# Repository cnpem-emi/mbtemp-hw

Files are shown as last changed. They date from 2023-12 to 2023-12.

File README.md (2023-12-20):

MBTemp
=====

MBTemp is an electronic board to acquire temperature in eight independent channels. It has been developed by the Control Group of Brazilian Synchrotron Light Laboratory (LNLS).

Example
-------

An example of use is present in the well documented file `exemplo-mbtemp.py`.

Contacts
-------------------------------------

Any doubts related to this projects, please do not hesitate to contact Robert Polli (robert.polli@cnpem.br)

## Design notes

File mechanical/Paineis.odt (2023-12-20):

PAINEL MBTemp

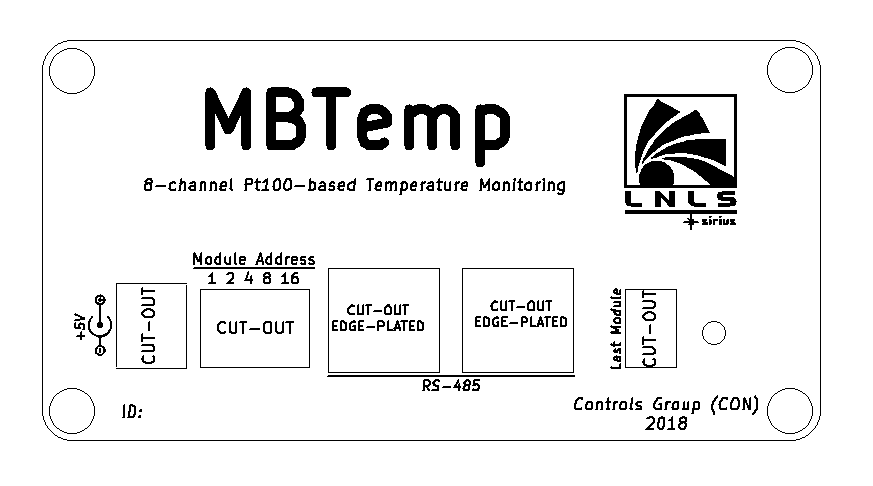
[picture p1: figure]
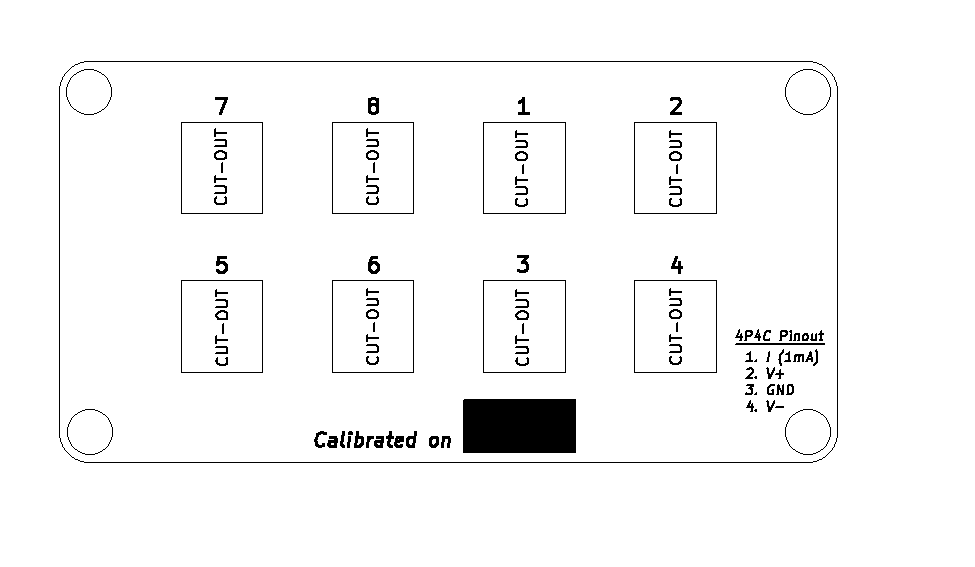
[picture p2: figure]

PAINEL MBTemp

v2

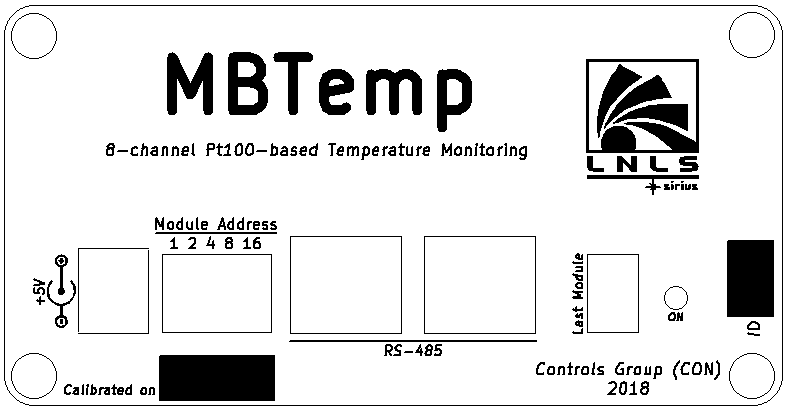
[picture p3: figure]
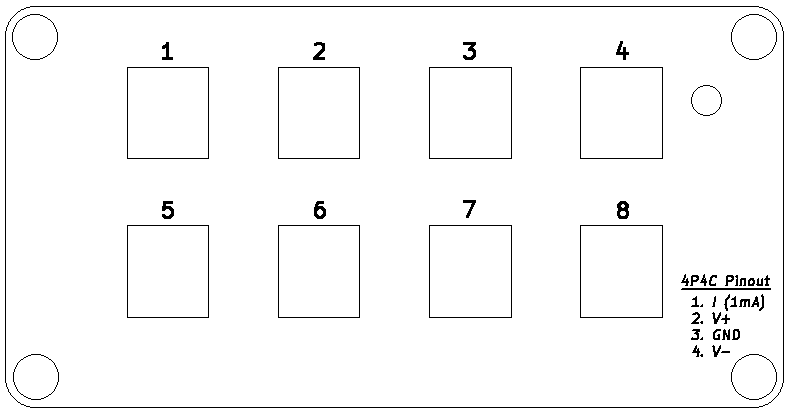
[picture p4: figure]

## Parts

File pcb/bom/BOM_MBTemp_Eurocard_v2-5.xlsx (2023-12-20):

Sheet: MBTemp3_Eurocard
Designator | Description | Value | Part Number | Package | Manufacturer | Quantity | PN CNPEM | Obs
C13,C12 | Ceramic Capacito 20pF 50V 5% SMD 0805 NP0 | 20pF | CL21C200JBANNNC | 0805 | Samsung ElectroMechanics | 2 | MT104425
C25 | Ceramic Capacitor 56pF 50V 5% SMD 0805 NP0 | 56pF | CL21C560JBANNNC | 0805 | Samsung ElectroMechanics | 1 | MT104427
C26,C23,C21,C17,C29,C34 | Multilayer Ceramic Capacitor 100nF 50V ±5% SMD 0805 X7R | 100nF | 08055C104JAT2A | 0805 | AVX | 6 | MT104382
C27,C24,C22,C18,C2,C15,C14,C1,C8,C11,C201,C37,C39,C47,C48,C41,C42,C45,C46,C61,C60,C59,C58,C57,C56,C55,C54 | Ceramic Capacitor 10uF 16V ±10% SMD 0805 X5R | 10uF | CL21A106KOQNNNE | 0805 | Samsung ElectroMechanics | 27 | MT104058
C28 | Aluminium Radial Capacitor 470uF 16V 20% PTH | 470uF | ECA-1CM471 | Radial Can | Panasonic Electronic Components | 1 | MT104059
C30,C31,C32,C3,C16,C10,C9,C38,C43,C44,C53,C20,C19 | Ceramic Capacitor 1uF 16V ±5% SMD 0805 X7R | 1u | C0805C105J4RACTU | 0805 | Kemet | 13 | MT104060
C33,C35 | Multilayer Ceramic Capacitor 47nF 100V 5% SMD 0805 X7R | 47nF | 08051C473JAT2A | 0805 | AVX | 2 | MT104243
C36 | Tantalum Capacitor 10uF, 10V, 10%, ESR 3.8ohm | 10uF | T491A106K010AT7280 | 1206 | Kemet | 1 | AP111595
C4,C7 | Ceramic Capacitor 4.7uF 50V 10% SMD 1210 X7R | 4.7uF | GRM32ER71H475KA88L | 1210 | Murata | 2 | MT104428
C40,C49 | Ceramic Capacitor 22nF 100V 5% SMD 0805 X7R | 22n | 08051C223JAT2A | 0805 | Murata | 2 | MT104429
C50,C51,C52 | Ceramic Capacitor 100pF 50V 5% SMD 0805 NP0 | 100pF | C0805C101J5GACTU | 0805 | Kemet | 3 | MT104242
C6,C5 | Ceramic Capacitor 10nF 50V 5% SMD 0805 C0G | 10nF | GRM2195C1H103JA01D | 0805 | Murata | 2 | AP111901
D1 | Green LED, 2.1V, 20mA, SMD 0805 | LED Green | LTST-C171GKT | 0805 | Lite-On Inc | 1 | AP111654
D2 | LED Circuit Board Indicator Single Red Diffused, Through Hole, Right Angle | LED Red | WP934CB/ID | 2x1 PTH pitch 2,54mm | Kingbright | 1 | AP110389
D4,D5 | Diodo Schottky 20V 500mA DC SMD 0805 | Diode Sch | SD0805S020S0R5 | 0805 | AVX Corporation | 2 | AP103285
J4,J3,J6,J5 | RJ11 Jack connector Right Angle | RJ11 | TM5RJ3-44(50) | 4P4C | Hirose Electric Co | 4 | AP110402
J9,J10 | RJ25 | RJ25 | 133623 | 6P6C | ERNI | 2 | AP109847
JP1 | Dip Switch SPST 2 Position Through Hole, Right Angle Slide (Standard) Actuator 25mA 24VDC | DIP switch 2pos Right Angle | KAS2102E | DIP Switch Right Angle PTH | E-Switch | 1 | AP110400
K1 | Power Barrel Jack Connector 2mm ID, 5.5mm OD, PTH, right angle | Jack | PJ-002AH | Jack J4-5.5mm 2.0mm | CUI Inc | 1 | MT104062
L2,L1 | 6.8uH shielded wirewound Inductor 850mA 288mOhm | 6.8uH | LQH32PN6R8NN0L | 1210 | Murata | 2
P1 | DIP Switch slide 5 positions SPST right angle PTH | DIP Switch slide SPST right angle PTH | KAS2105E | PIN_ARRAY_5x2 | E-Switch | 1 | MT103732
P2 | 10 positions Male Header, PTH, Shrouded Connector, Pitch 2.54mm | Header 2x05 | 302-S101 | Straight_2x05 Shrouded pitch 2.54mm | On Shore Technology Inc | 1 | AP103279
P3 | Conector 2x10 pitch 2.54mm | CONN_02X10 | DW-10-09-F-D-425 | Pin_Header_Straight_2x10 | Samtec | 1 | MT104063
P4 | Pino de testes | 1 pin |  | Pin Header Straight 1x1 |  | 1 | ---- | NÃO DEVE SER MONTADO/COMPRADO
R1 | Resistor 22K ohm 0,1% 1/8W SMD 0805 Thin Film | 22kΩ | ERA-6AEB223V | 0805 | Panasonic Electronic Components | 1 | MT104109
R17,R16,R24,R36,R45,R27 | Resistor Jumper 0 ohm 1% 1/8W SMD 0805 Thick Film | 0Ω | RC0805JR-070RL | 0805 | Yageo | 6 | MT100803
R19,R18,R25,R35,R44,R32 | Resistor Jumper 0 ohm 1% 1/8W SMD 0805 Thick Film | 0 | RC0805JR-070RL | 0805 | Yageo | 6 | ---- | NÃO DEVE SER MONTADO/COMPRADO
R2 | Resistor 100 ohm 0,1% 1/8W SMD 0805 Thin Film | 100Ω | ERA-6AEB101V | 0805 | Panasonic Electronic Components | 1 | MT104084
R20,R14 | Resistor 1 Mohm 1% 1/8W SMD 0805 Thick Film | 1MΩ | RC0805FR-071ML | 0805 | Yageo | 2 | MT104430
R15,R5 | Resistor 1K ohm 0,1% 1/8W SMD 0805 Thin Film | 1kΩ | ERA-6AEB102V | 0805 | Panasonic Electronic Components | 2 | MT104085
R21,R22 | Resistor 1K ohm 1% 1/8W SMD 0805 Thick Film | 1kΩ | RC0805FR-071KL | 0805 | Yageo | 2 | MT104228
R23 | Resistor 470 ohm 1% 1/8W SMD 0805 Thick Film | 470Ω | RC0805FR-07470RL | 0805 | Yageo | 1 | MT104431
R40 | Resistor 620 ohm 1% 1/8W SMD 0805 Thick Film | 620Ω | RC0805FR-07620RL | 0805 | Yageo | 1 | MT104227
R29 | Resistor 2.2 k ohm 1% 1/8W SMD 0805 Thick Film | 2.2kΩ | RC0805FR-072K2L | 0805 | Yageo | 1 | MT104237
R3 | Resistor 120 ohm 0,1% 1/8W SMD 0805 Thin Film | 120Ω | ERA-6AEB121V | 0805 | Panasonic Electronic Components | 1 | MT104086
R26 | Resistor 120 ohm 1% 1/8W SMD 0805 Thick Film | 120Ω | RC0805FR-07120RL | 0805 | Yageo | 1 | MT104234
R30 | Resistor 33 k ohm 1% 1/8W SMD 0805 Thick Film | 33kΩ | RC0805FR-0733KL | 0805 | Yageo | 1 | MT104432
R31 | Resistor 4.7 k ohm 1% 1/8W SMD 0805 Thick Film | 4.7kΩ | RC0805FR-074K7L | 0805 | Yageo | 1 | MT104433
R34 | Resistor 910 k ohm 1% 1/8W SMD 0805 Thick Film | 910kΩ | RC0805FR-07910KL | 0805 | Yageo | 1 | MT104231
R38, R39 | Resistor 300k ohm ±0,1% 1/8W SMD 0805 Thin Film | 300kΩ | RT0805BRD07300KL | 0805 | Yageo | 1 | MT104087
R43 | Resistor 62 k ohm 1% 1/8W SMD 0805 Thick Film | 62kΩ | RC0805FR-0762KL | 0805 | Yageo | 1 | MT104434
R6,R7 | Resistor 6.2 k ohm 0,1% 1/8W SMD 0805 Thin Film | 6.2kΩ | ERA-6AEB622V | 0805 | Panasonic Electronic Components | 2 | MT104088
R8,R4 | Resistor 330 ohm, 0,1%, 1/8W, SMD 0805, Thin Film | 330Ω | ERA-6AEB331V | 0805 | Panasonic Electronic Components | 2 | MT104089
R9,R10,R11,R12,R13,R28,R42 | Resistor 10K ohm 1% 1/8W SMD 0805 Thick Film | 10kΩ | RC0805FR-0710KL | 0805 | Yageo | 7 | MT104235
SW1,SW2 | 3 positions header connector 0.1” PTH Gold | -5V / +6V | 961103-6404-AR | Pin_Header_Straight_1x03_Pitch2.54mm | 3M | 2 | MT104065
U10 | 5V Voltage Reference IC +/-0.05% 10mA | REF5050 | REF5050IDR | SOIC-8 | Texas Instruments | 1 | AP100206
U11 | General Purpose Amplifier 2 Circuit | OPA2277 | OPA2277UA/2K5 | SOIC-8 | Texas Instruments | 1 | AP102160
U12 | Differential Amplifier 1 Circuit Differential Rail-to-rail | AD8139 | AD8139ARDZ-REEL7 | SO-8 Expoded Pad | Analog Devices | 1 | AP103263
U13 | Analog to Digital Converter 16 bits SAR | ADS8318 | ADS8318IBDGST | MSOP-10 | Texas Instruments | 1 | AP103262
U14 | DCDC Converter IC, 1W, 5V output, 5V input | DCR010505U | DCR010505U/1K | SOIC-28 | Texas Instruments | 1 | AP109804
U15 | Linear Regulator LDO Adjustable Negative 1,5A | LT3015 | LT3015EMSE#PBF | MSOP-12 | Linear Technology | 1 | AP107414
U19 | Linear Regulator LDO Adjustable Negative 1,5A | LT3015 | LT3015EMSE#PBF | MSOP-12 | Linear Technology | 1 | ---- | NÃO DEVE SER MONTADO/COMPRADO
U16 | DCDC Converter IC, 1W, +/-12V output, 5V input | DCP010512D | DCP010512DBP-U | DCP010512D | Texas Instruments | 1 | AP106621
U9,U18 | Linear Voltage Regulator Adjustable IC, 0-36V, 1.1A, SMD SOT-223 | LT3080 | LT3080EST#TRPBF | SOT-223 | Linear Technology | 2 | MT104255
U17 | Linear Voltage Regulator Adjustable IC, 0-36V, 1.1A, SMD SOT-223 | LT3080 | LT3080EST#TRPBF | SOT-223 | Linear Technology | 1 | ---- | NÃO DEVE SER MONTADO/COMPRADO
U2,U1,U3 | Circuit IC Switch 8:1 120ohms | 74HC4051 | 74HC4051PW,118 | TSSOP-16 | NXP | 3 | AP103267
U4 | Current Source Regulator IC 200mA 1% | LT3092 | LT3092EST#PBF | SOT-223 | Linear Technology | 1 | AP103266
U5 | 2.5V Voltage Reference IC +/-1% 10mA | REF5025 | REF5025AQDRQ1 | SOIC-8 | Texas Instruments | 1 | AP103265
U6 | RS422/485 Digital Isolator IC, 2500Vrms, 40Mbps, SMD SOIC-16 | IL3685 | IL3685E | SOIC-16 | NVE | 1 | AP102999
U7 | PIC 16F Microcontroller 8-bit 20MHz 14kB Flash | PIC16F887A_TQFP | PIC16F887-I/PT | TQFP-44 | Microchip Technology | 1 | AP103857
U8 | Switching regulator Buck-Boost Adjustable | LT3582 | LT3582EUD#PBF | WFQFN-16 | Linear Technology | 1 | AP100196
X1 | 16MHz +/- 30ppm Crystal 20pF 40ohm SMD | CRYSTAL 16MHz | ECS-160-20-5PX-TR | CrystalSMD HC49/US | ECS Inc | 1 | MT104066
F1,F2,F3,F4 | Fiducial 1mm | NA | NA | NA | NA | 4

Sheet: MBTemp_Stack
Designator | Description | Value | Part Number | Package | Manufacturer | Quantity | PNCNPEM | Obs
J2,J1,J8,J7 | RJ11 Jack connector Right Angle | RJ11 | TM5RJ3-44(50) | 4P4C | Hirose Electric Co | 4 | AP110402
P3 | Conector 2x10 pitch 2.54mm | CONN_02X10 | SSQ-110-03-F-D | Pin_Header_Straight_2x10 | Samtec | 1 | MT104067
C1,C2,C3,C4,C5,C6,C7,C8 | Ceramic Capacitor 10uF 16V ±10% SMD 0805 X5R | 10uF | CL21A106KOQNNNE | 0805 | Samsung ElectroMechanics | 8 | MT104058
F1,F2,F3,F4 | Fiducial 1mm | NA | NA | NA | NA | 4
 |  |  |  |  |  | "

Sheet: Montagem Mecanica
Designator | Description | Value | Part Number | Package | Manufacturer | Quantity | PN CNPEM | Obs
MH5,MH6,MH7 | Montagem Mecânica M3 | Espaçador 19mm M3x0.5 steel | 971190321 | M3 | Wurth Electronics Inc | 3 | MT103722
 |  | MACHINE SCREW PAN PHILLIPS M3 | MPMS 003 0005 PH | M3 | B&F Fastener Supply | 3 | AO104596
 |  | HEX NUT 0.217" M3 | MHNZ 003 | M3 | B&F Fastener Supply | 3 | MT103727
 |  | Arruela para parafusos M3 | MFWZ 003 | M3 | B&F Fastener Supply | 6 | MT103728 | Para colocar no parafuso e porca
Jumper | Jumper for SW1 and SW2 | Connector jumper 2.54mm – Flash Gold | QPC02SXGN-RC | Jumper | Sullins Connector | 2 |  | Conectado ao pino “LIN”

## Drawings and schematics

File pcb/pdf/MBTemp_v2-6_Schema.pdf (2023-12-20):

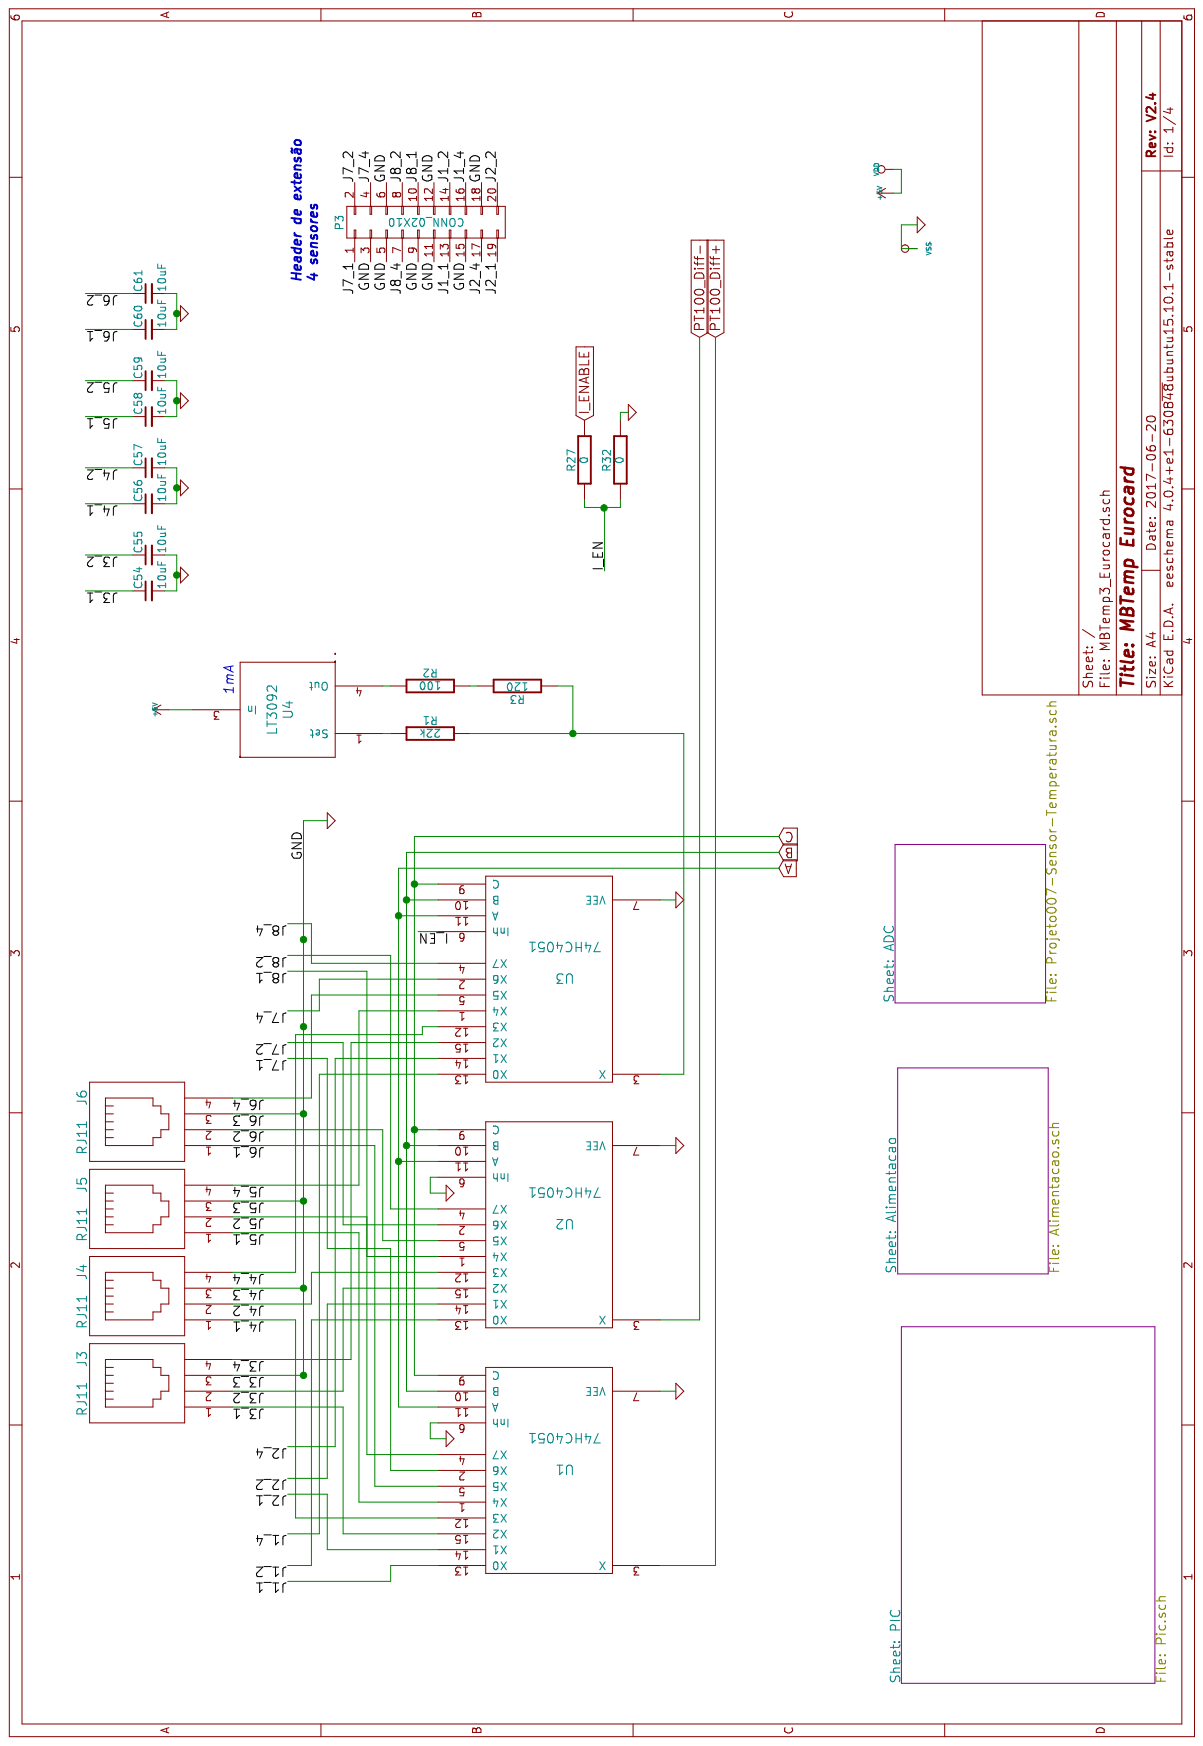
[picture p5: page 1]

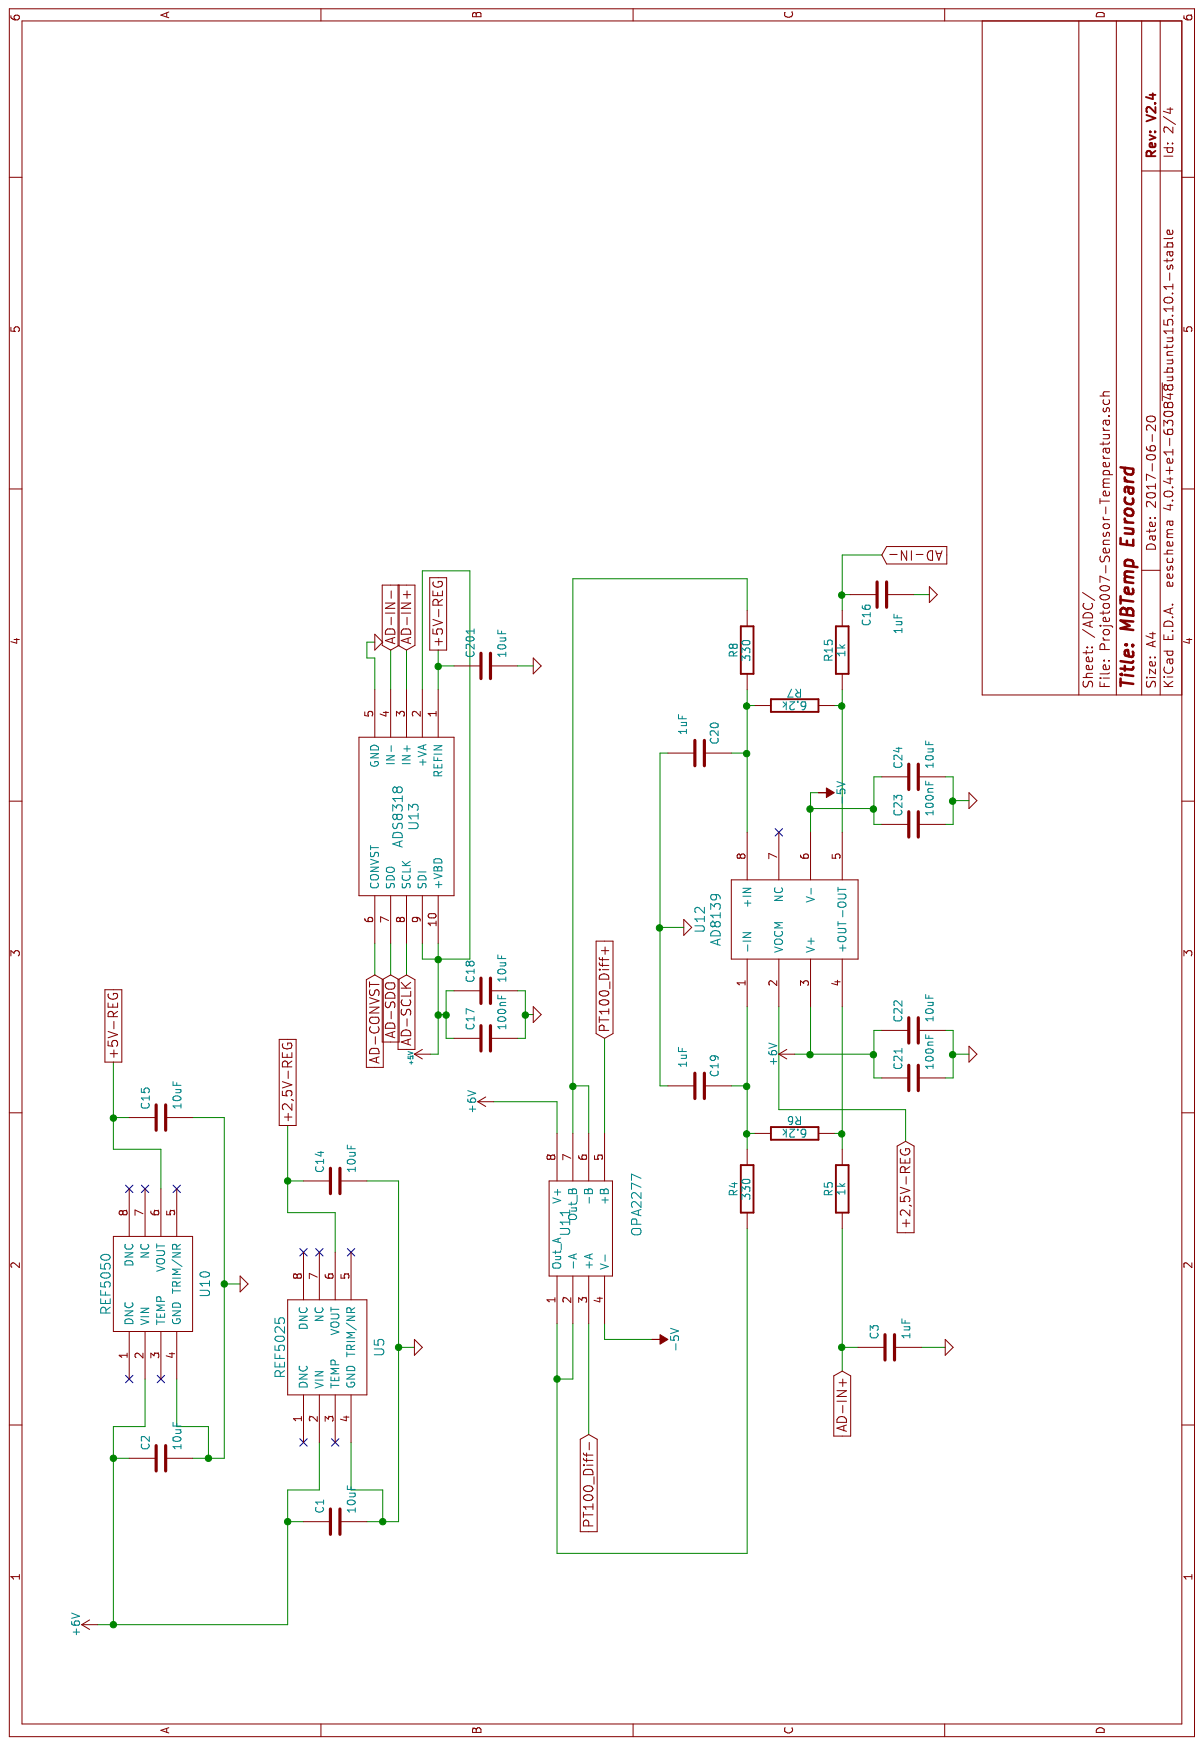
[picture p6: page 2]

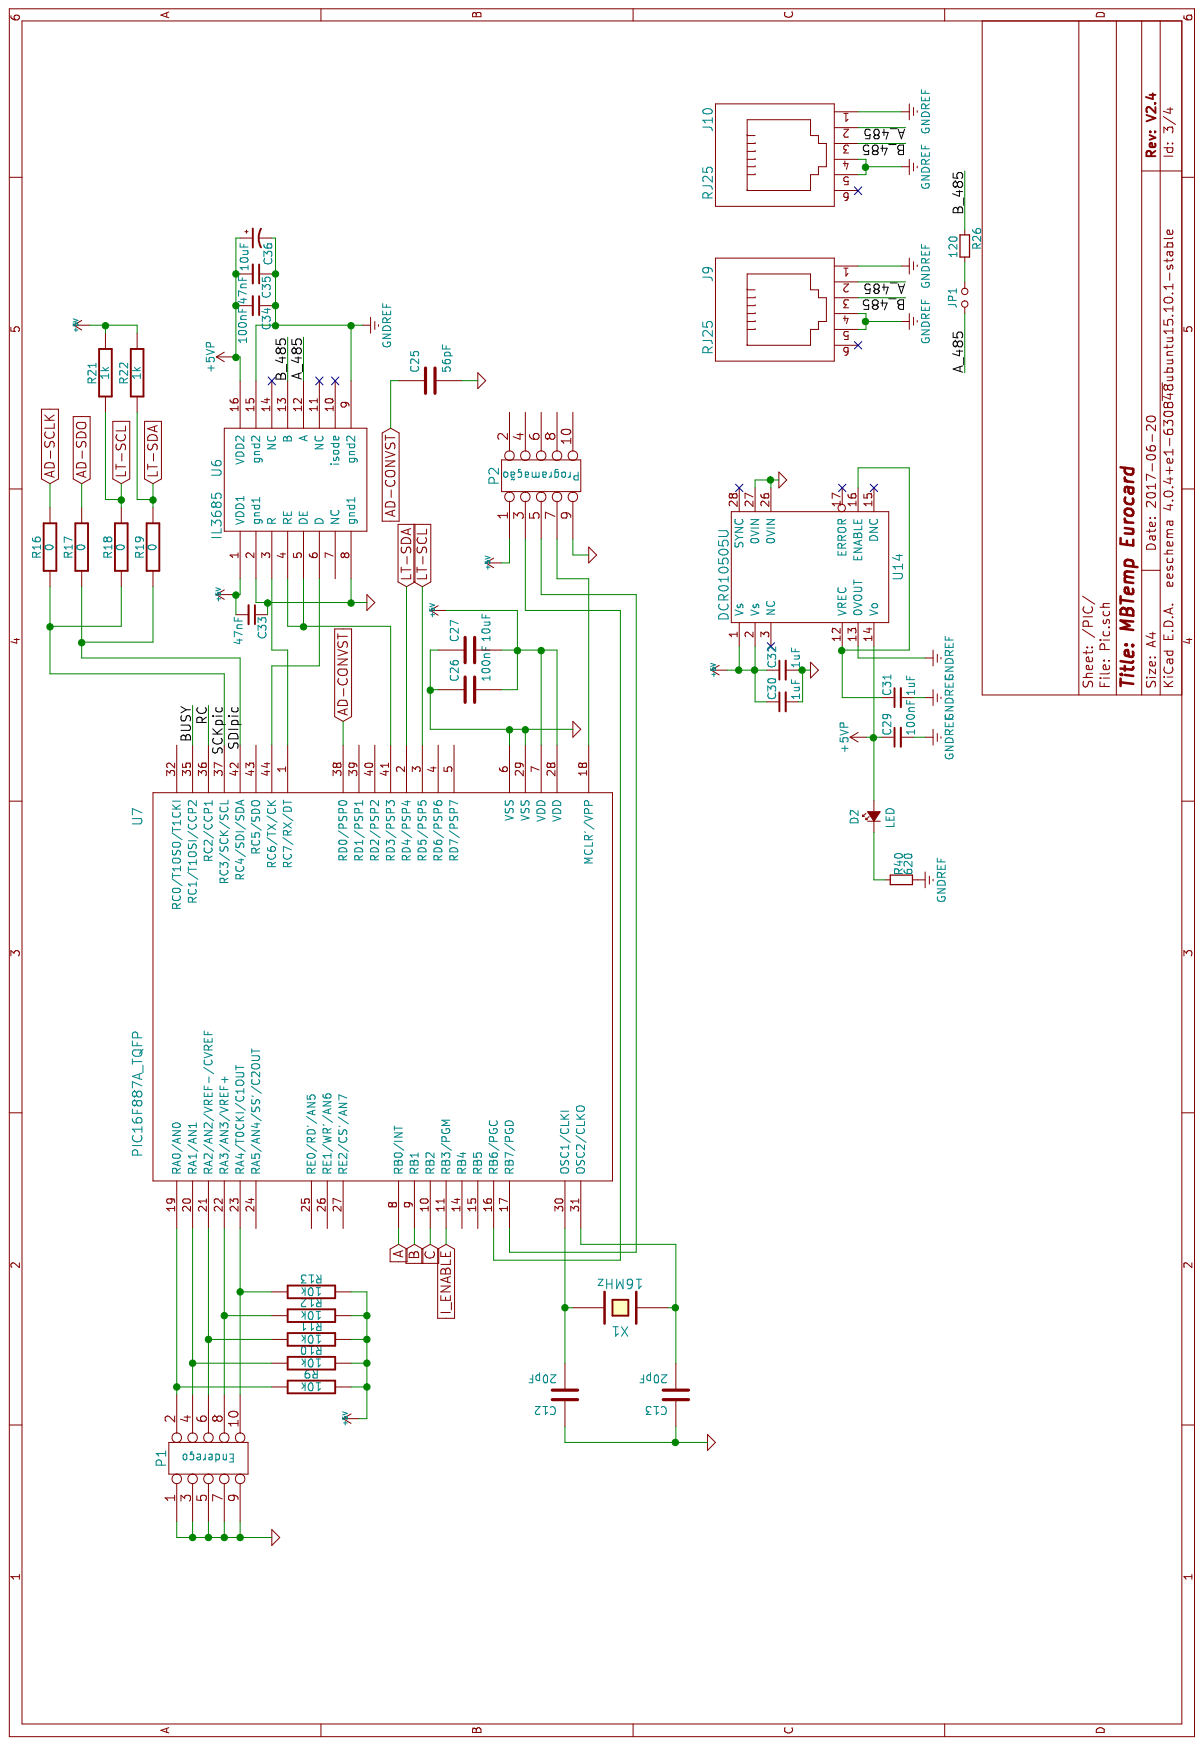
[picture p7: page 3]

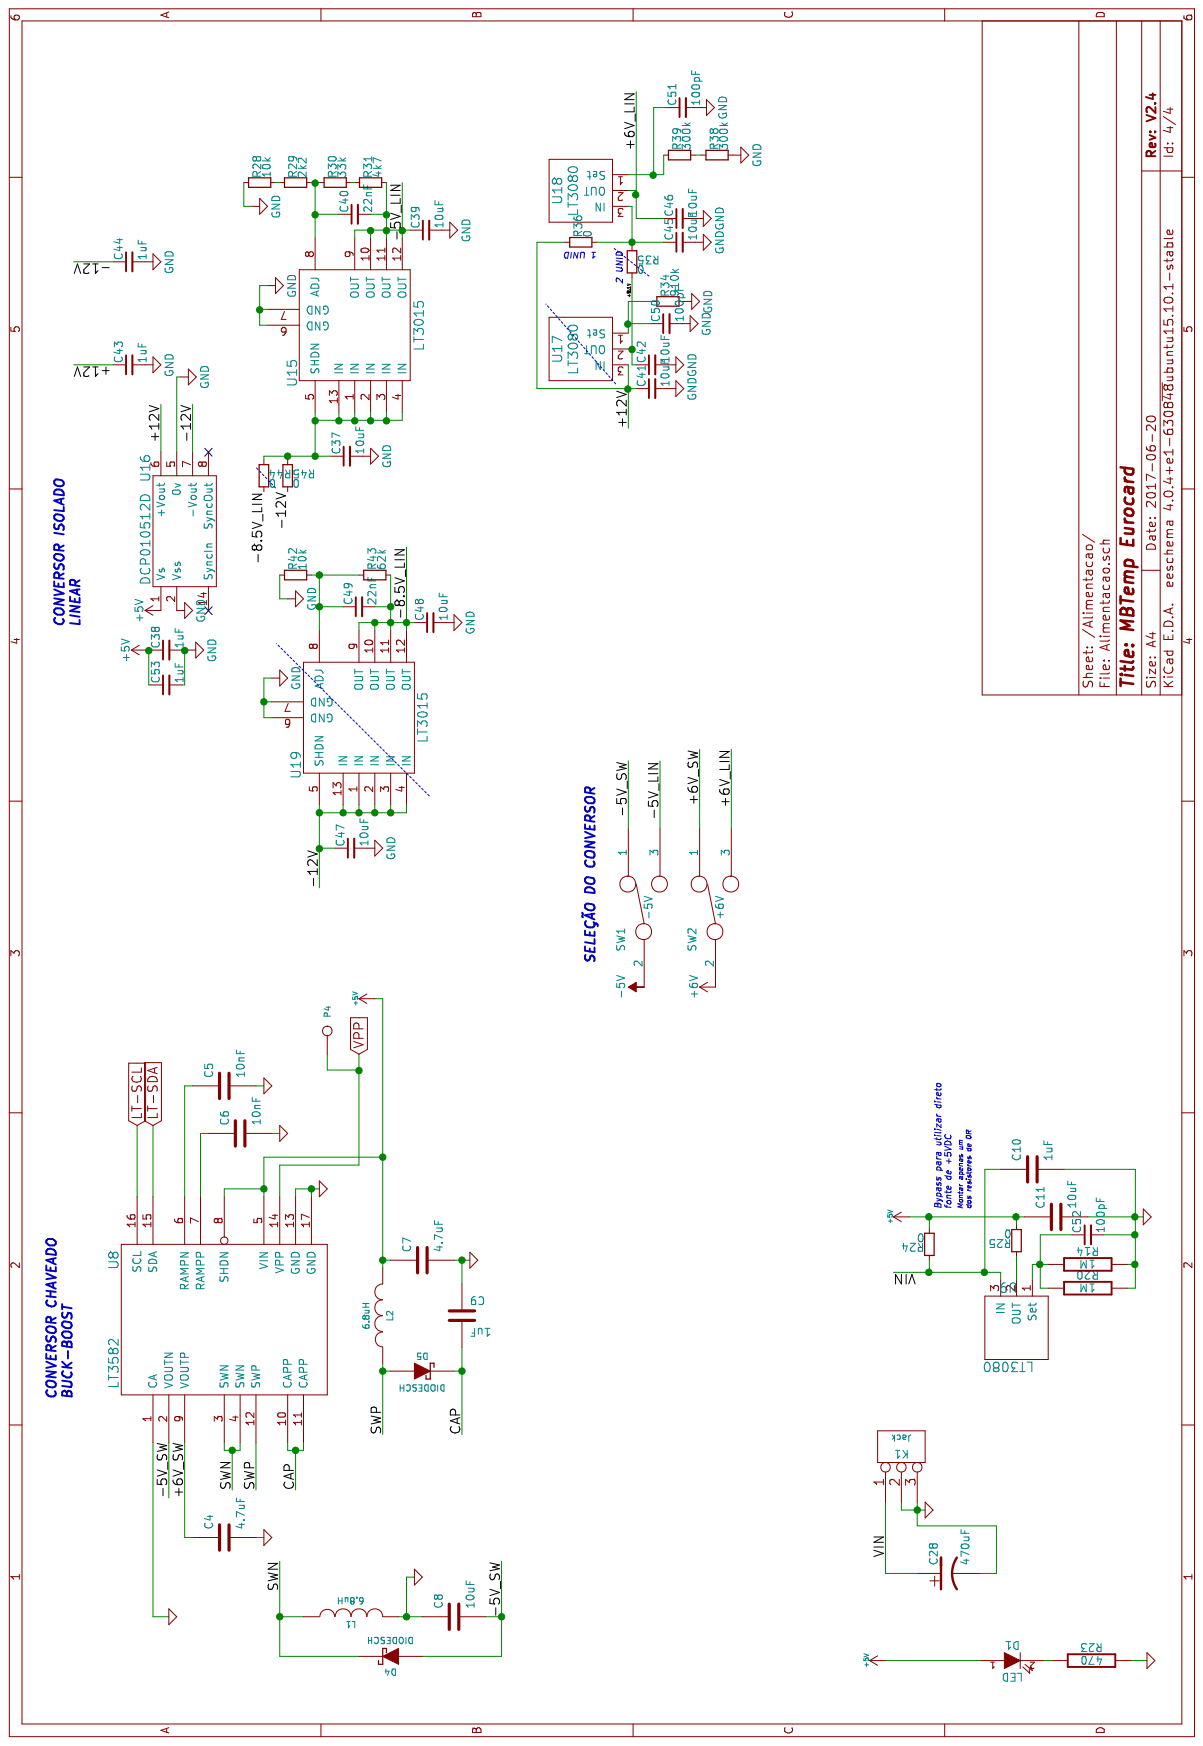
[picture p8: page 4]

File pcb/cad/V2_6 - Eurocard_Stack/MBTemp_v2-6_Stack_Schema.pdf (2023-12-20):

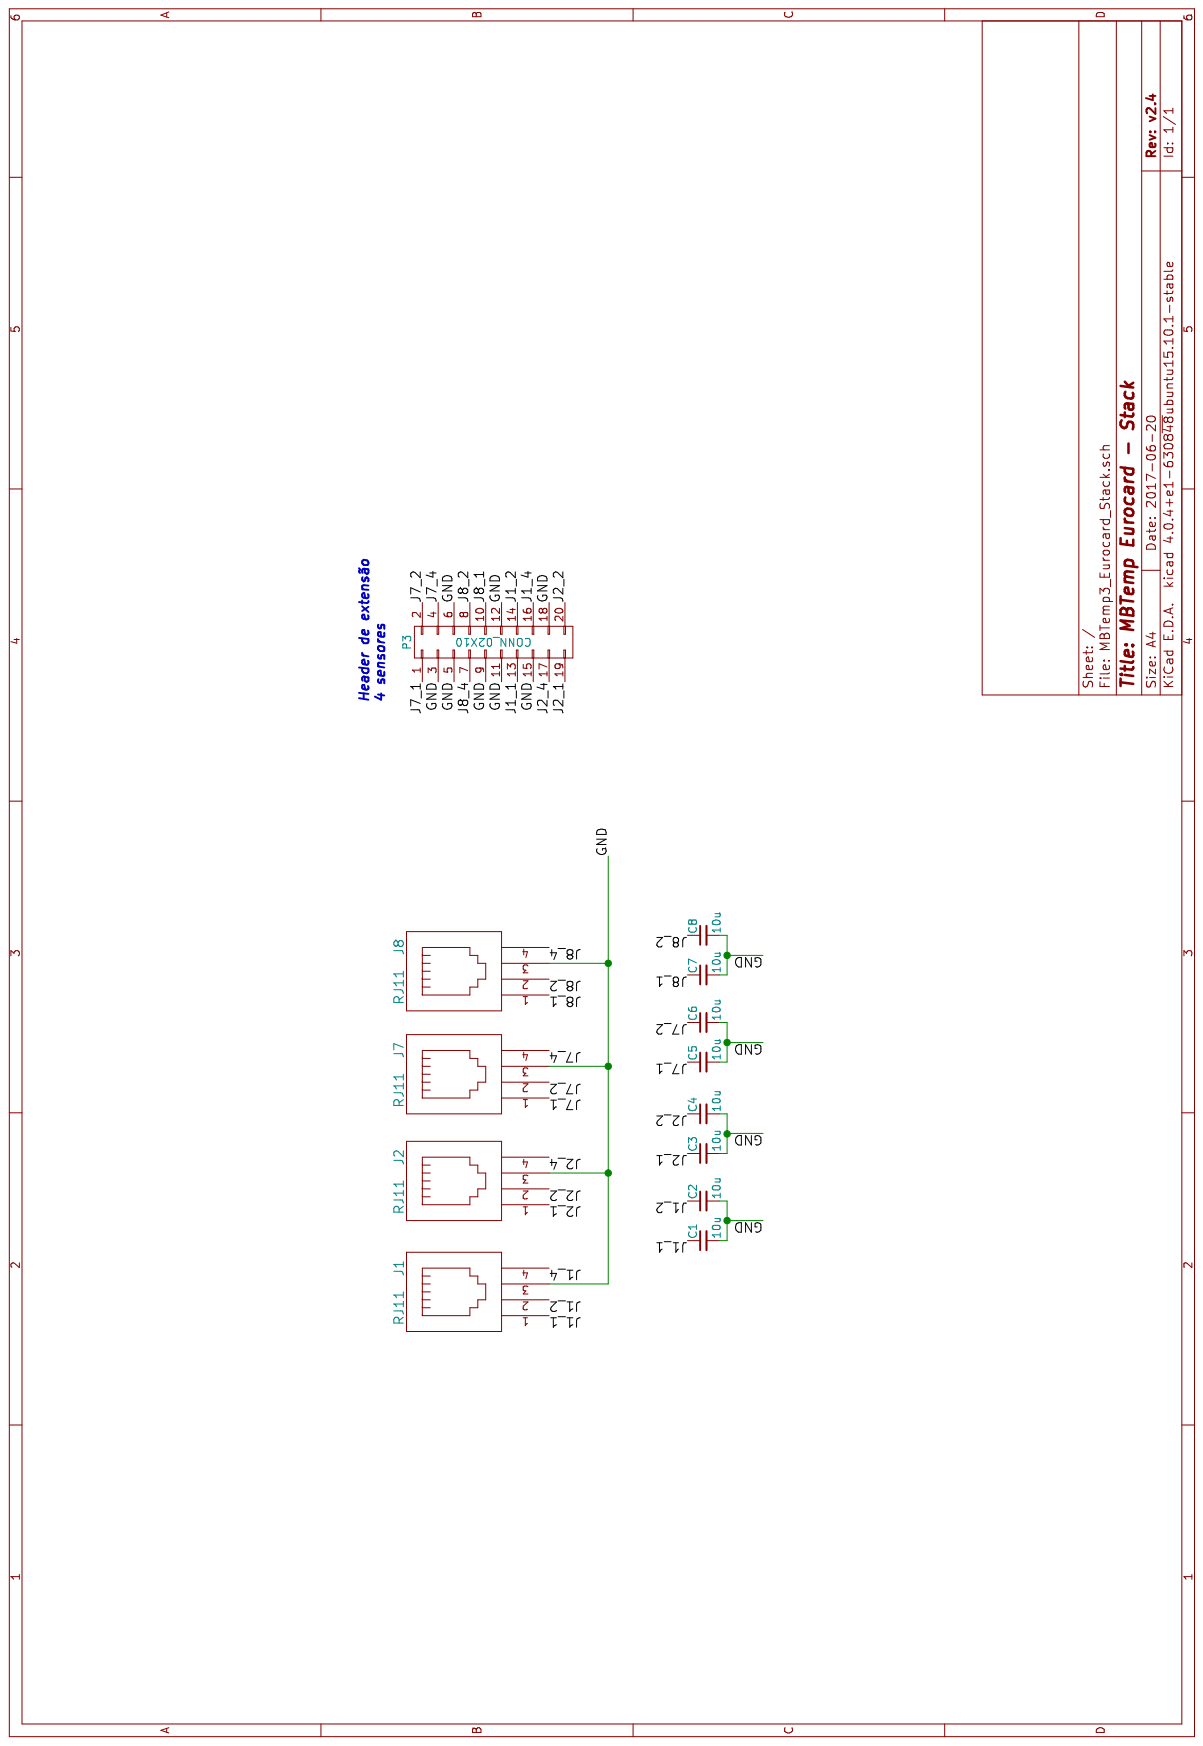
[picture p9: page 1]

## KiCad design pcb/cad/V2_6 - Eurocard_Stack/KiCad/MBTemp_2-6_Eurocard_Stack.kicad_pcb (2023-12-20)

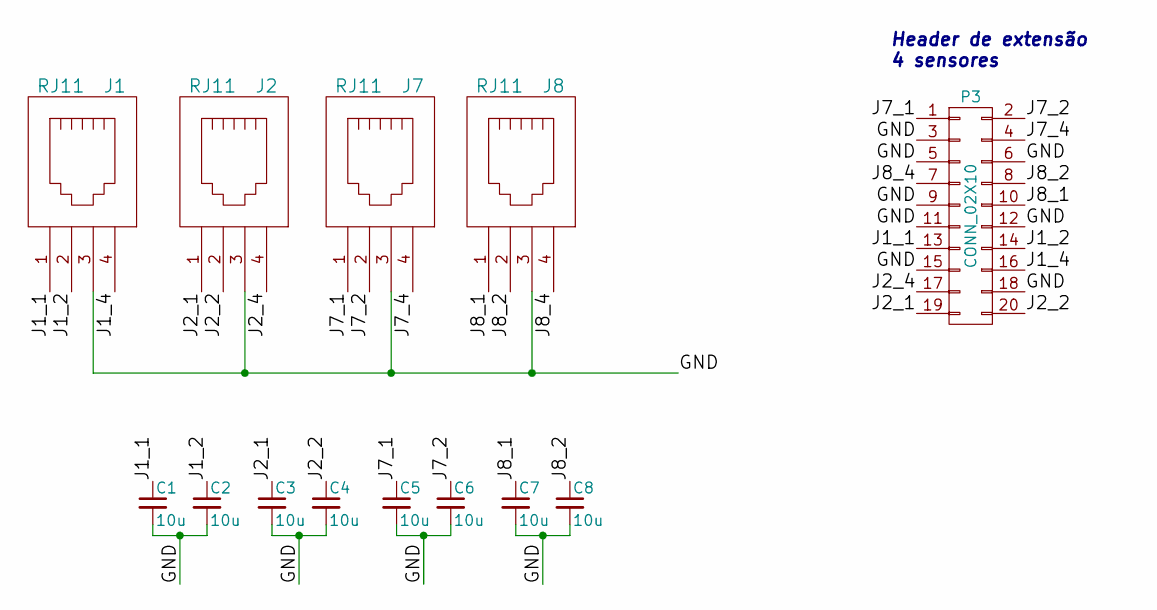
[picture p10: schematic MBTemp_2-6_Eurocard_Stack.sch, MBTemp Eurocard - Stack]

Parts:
C1, C2, C3, C4, C5, C6, C7, C8: 10u; C_0805
J1, J2, J7, J8: RJ11
P3: CONN_02X10; Pin_Header_Straight_2x10

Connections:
/GND: C1.2, C2.2, C3.2, C4.2, C5.2, C6.2, C7.2, C8.2, J1.3, J2.3, J7.3, J8.3, P3.3, P3.5, P3.6, P3.9, P3.11, P3.12, P3.15, P3.18; also elsewhere on the board
/J1_1: C1.1, J1.1, P3.13
/J1_2: C2.1, J1.2, P3.14
/J1_4: J1.4, P3.16
/J2_1: C3.1, J2.1, P3.19
/J2_2: C4.1, J2.2, P3.20
/J2_4: J2.4, P3.17
/J7_1: C5.1, J7.1, P3.1
/J7_2: C6.1, J7.2, P3.2
/J7_4: J7.4, P3.4
/J8_1: C7.1, J8.1, P3.10
/J8_2: C8.1, J8.2, P3.8
/J8_4: J8.4, P3.7

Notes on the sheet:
Header de extensão 4 sensores

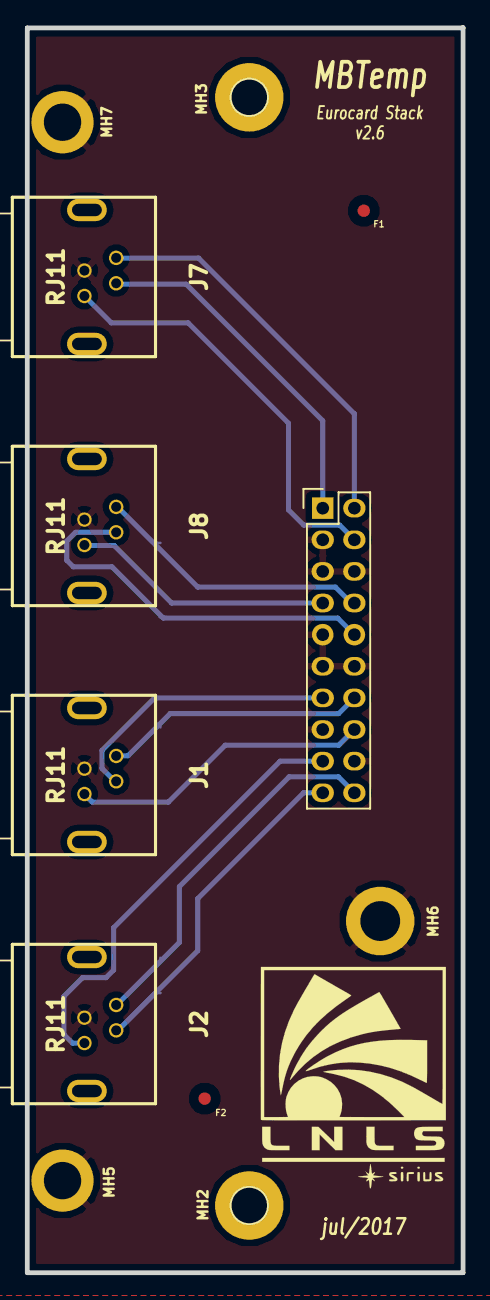
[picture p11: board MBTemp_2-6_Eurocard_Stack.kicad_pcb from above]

Board: 2 copper layers, 35.0 x 100.0 mm, 18 parts (0 on the bottom side), 13 nets.

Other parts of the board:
F1, F2, F3, F4: Fiducial_1mm_Dia_2.54mm_Outer_CopperBottom
P?: C64AC; Eurocard_template

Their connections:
/GND: P?.1, P?.2; also elsewhere on the board

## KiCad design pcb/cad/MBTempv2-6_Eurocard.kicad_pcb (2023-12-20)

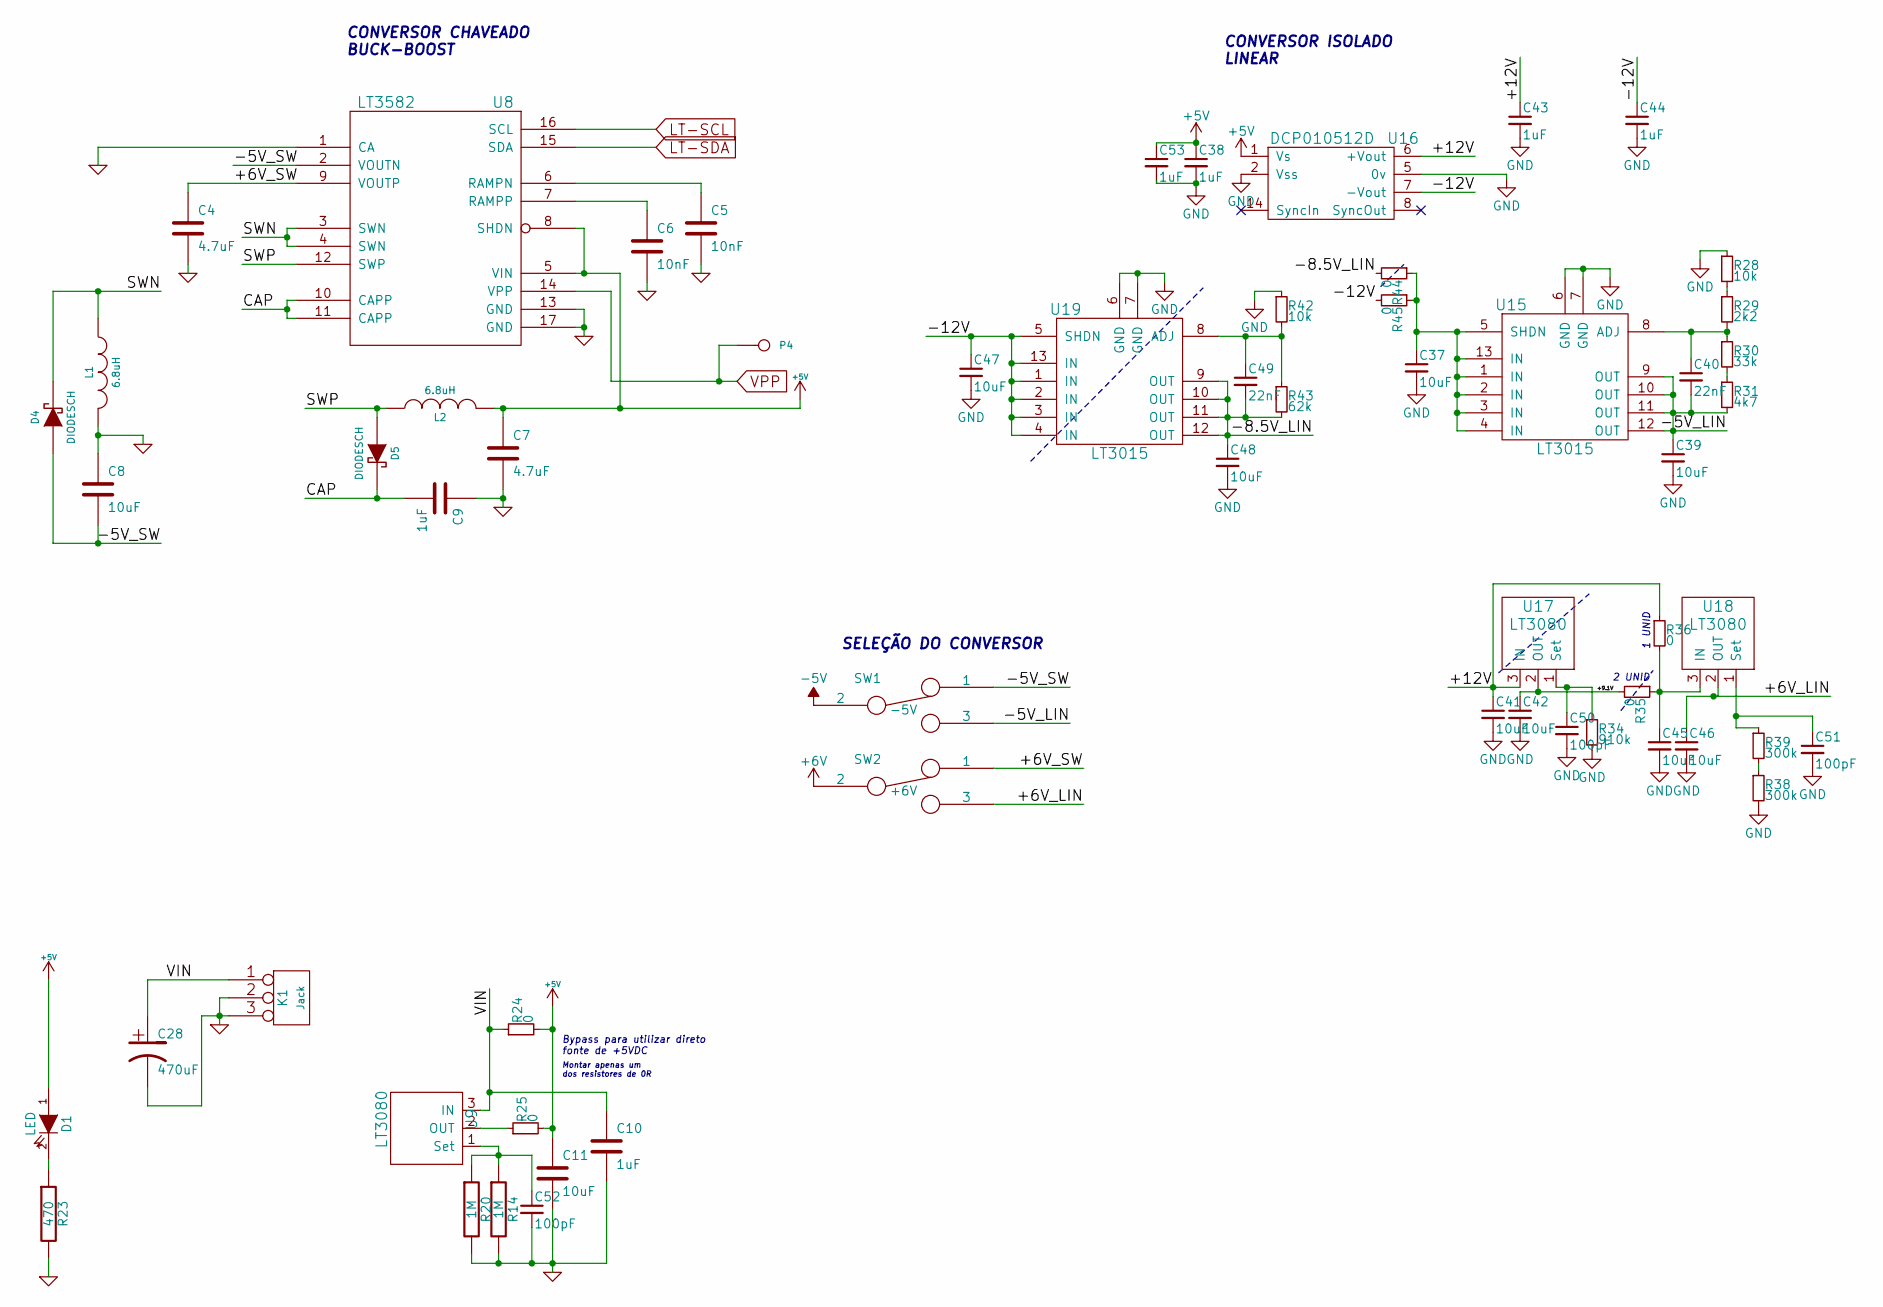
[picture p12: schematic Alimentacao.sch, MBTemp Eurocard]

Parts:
C4, C7: 4.7uF
C5, C6: 10nF
C8, C11: 10uF
C9, C10: 1uF
C28: 470uF
C37, C39, C41, C42, C45, C46, C47, C48: 10uF; C_0805
C38, C43, C44, C53: 1uF; C_0805
C40, C49: 22nF; C_0805
C50, C51, C52: 100pF; C_0805
D1: LED
D4, D5: DIODESCH
K1: Jack
L1, L2: 6.8uH
P4: CONN_1
R14, R20: 1M
R23: 470
R24, R25, R35, R36, R44, R45: 0; R_0805
R28, R42: 10k; R_0805
R29: 2k2; R_0805
R30: 33k; R_0805
R31: 4k7; R_0805
R34: 910k; R_0805
R38, R39: 300k; R_0805
R43: 62k; R_0805
SW1: -5V; Pin_Header_Straight_1x03_Pitch2.54mm
SW2: +6V; Pin_Header_Straight_1x03_Pitch2.54mm
U8: LT3582
U9: LT3080
U15, U19: LT3015; MSOP-12-1EP_3x4mm_Pitch0.65mm
U16: DCP010512D; DCP0105xxD
U17, U18: LT3080; SOT-223

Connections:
+5V: C7.1, C11.1, C38.1, C53.1, D1.1 (A), L2.2, R24.2, R25.2, U8.5 (VIN), U8.8 (SHDN), U16.1 (Vs); also elsewhere on the board
+6V: SW2.2; also elsewhere on the board
-5V: SW1.2; also elsewhere on the board
/Alimentacao/+6V_LIN: C46.1, SW2.3, U18.2 (OUT)
/Alimentacao/+6V_SW: C4.1, SW2.1, U8.9 (VOUTP)
/Alimentacao/+9.1V: C42.1, R35.2, U17.2 (OUT)
/Alimentacao/+12V: C41.1, C43.1, R36.1, U16.6 (+Vout), U17.3 (IN)
/Alimentacao/-5V_LIN: C39.1, C40.2, R31.2, SW1.3, U15.9 (OUT), U15.10 (OUT), U15.11 (OUT), U15.12 (OUT)
/Alimentacao/-5V_SW: C8.2, D4.1 (A), SW1.1, U8.2 (VOUTN)
/Alimentacao/-8.5V_LIN: C48.1, C49.2, R43.2, R44.2, U19.9 (OUT), U19.10 (OUT), U19.11 (OUT), U19.12 (OUT)
/Alimentacao/-12V: C44.1, C47.1, R45.2, U16.7 (-Vout), U19.1 (IN), U19.2 (IN), U19.3 (IN), U19.4 (IN), U19.5 (SHDN), U19.13 (IN)
/Alimentacao/CAP: C9.2, D5.2 (K), U8.10 (CAPP), U8.11 (CAPP)
/Alimentacao/SWN: D4.2 (K), L1.1, U8.3 (SWN), U8.4 (SWN)
/Alimentacao/SWP: D5.1 (A), L2.1, U8.12 (SWP)
/Alimentacao/VIN: C10.1, C28.1, K1.1, R24.1, U9.3 (IN)
GND: C4.2, C5.2, C6.2, C7.2, C8.1, C9.1, C10.2, C11.2, C28.2, C37.2, C38.2, C39.2, C41.2, C42.2, C43.2, C44.2, C45.2, C46.2, C47.2, C48.2, C50.2, C51.2, C52.2, C53.2, K1.2 (PM), K1.3, L1.2, R14.2, R20.2, R23.2, R28.1, R34.2, R38.2, R42.1, U8.1 (CA), U8.13 (GND), U8.17 (GND), U15.6 (GND), U15.7 (GND), U16.2 (Vss), U16.5 (0v), U19.6 (GND), U19.7 (GND); also elsewhere on the board
LT-SCL: U8.16 (SCL); also elsewhere on the board
LT-SDA: U8.15 (SDA); also elsewhere on the board
unnamed: C5.1, U8.6 (RAMPN)
unnamed: C6.1, U8.7 (RAMPP)
unnamed: C37.1, R44.1, R45.1, U15.1 (IN), U15.2 (IN), U15.3 (IN), U15.4 (IN), U15.5 (SHDN), U15.13 (IN)
unnamed: C40.1, R29.2, R30.1, U15.8 (ADJ)
unnamed: C45.1, R35.1, R36.2, U18.3 (IN)
unnamed: C49.1, R42.2, R43.1, U19.8 (ADJ)
unnamed: C50.1, R34.1, U17.1 (Set)
unnamed: C51.1, R39.1, U18.1 (Set)
unnamed: C52.1, R14.1, R20.1, U9.1 (Set)
unnamed: D1.2 (K), R23.1
unnamed: R25.1, U9.2 (OUT)
unnamed: R28.2, R29.1
unnamed: R30.2, R31.1
unnamed: R38.1, R39.2
VPP: P4.1, U8.14 (VPP)

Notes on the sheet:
Bypass para utilizar direto fonte de +5VDC
Montar apenas um dos resistores de 0R
1 UNID
2 UNID
CONVERSOR CHAVEADO BUCK-BOOST
CONVERSOR ISOLADO LINEAR
SELEÇÃO DO CONVERSOR

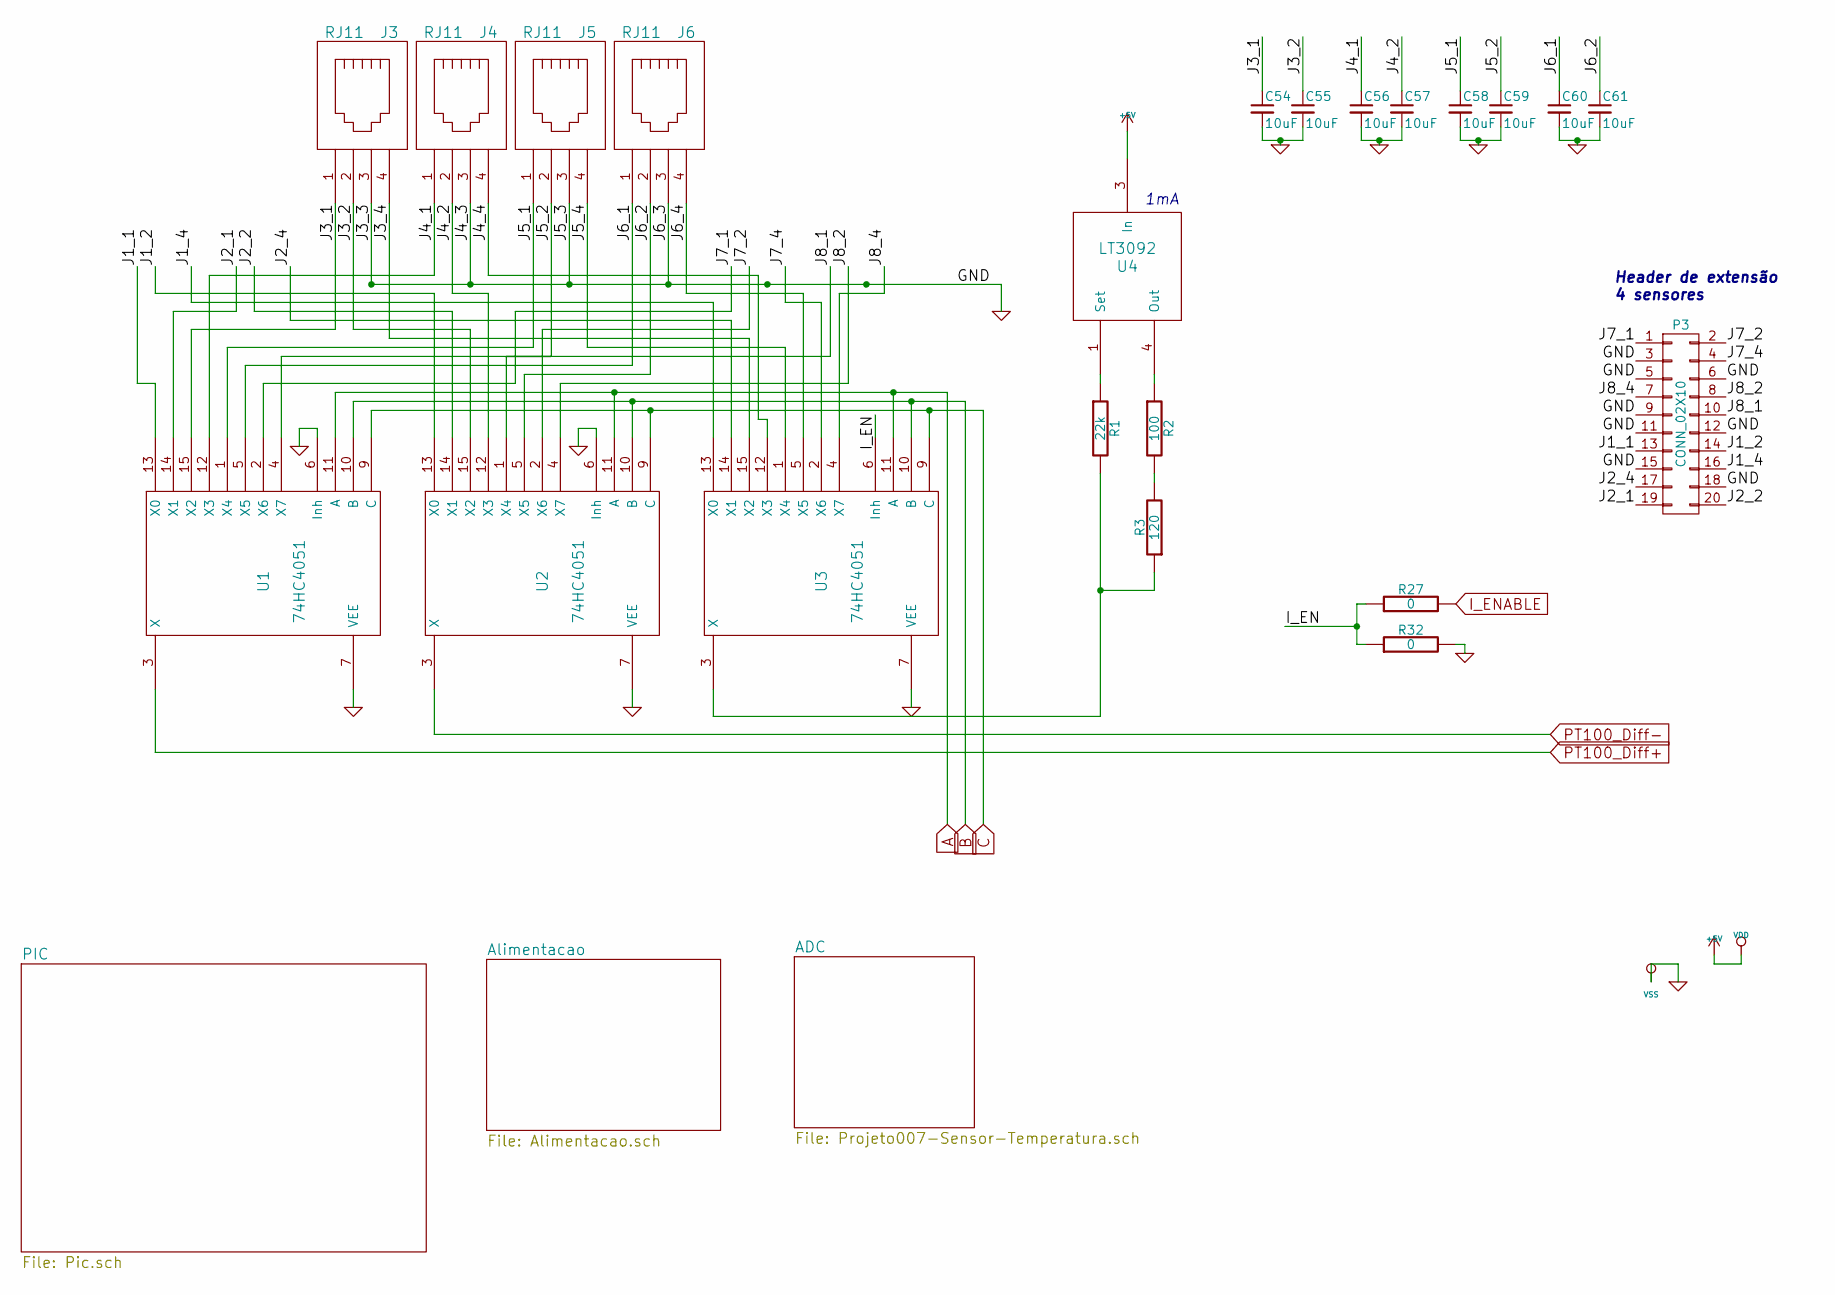
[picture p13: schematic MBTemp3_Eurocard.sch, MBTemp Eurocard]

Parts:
C54, C55, C56, C57, C58, C59, C60, C61: 10uF
J3, J4, J5, J6: RJ11
P3: CONN_02X10; Pin_Header_Straight_2x10
R1: 22k
R2: 100
R3: 120
R27, R32: 0
U1, U2, U3: 74HC4051
U4: LT3092

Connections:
+5V: U1.16 (VDD), U2.16 (VDD), U3.16 (VDD), U4.3 (In); also elsewhere on the board
/I_EN: R27.1, R32.1, U3.6 (Inh)
/J1_1: P3.13, U1.13 (X0)
/J1_2: P3.14, U2.13 (X0)
/J1_4: P3.16, U3.13 (X0)
/J2_1: P3.19, U1.14 (X1)
/J2_2: P3.20, U2.14 (X1)
/J2_4: P3.17, U3.14 (X1)
/J3_1: C54.1, J3.1, U1.15 (X2)
/J3_2: C55.1, J3.2, U2.15 (X2)
/J3_4: J3.4, U3.15 (X2)
/J4_1: C56.1, J4.1, U1.12 (X3)
/J4_2: C57.1, J4.2, U2.12 (X3)
/J4_4: J4.4, U3.12 (X3)
/J5_1: C58.1, J5.1, U1.1 (X4)
/J5_2: C59.1, J5.2, U2.1 (X4)
/J5_4: J5.4, U3.1 (X4)
/J6_1: C60.1, J6.1, U1.5 (X5)
/J6_2: C61.1, J6.2, U2.5 (X5)
/J6_4: J6.4, U3.5 (X5)
/J7_1: P3.1, U1.2 (X6)
/J7_2: P3.2, U2.2 (X6)
/J7_4: P3.4, U3.2 (X6)
/J8_1: P3.10, U1.4 (X7)
/J8_2: P3.8, U2.4 (X7)
/J8_4: P3.7, U3.4 (X7)
A: U1.11 (A), U2.11 (A), U3.11 (A); also elsewhere on the board
B: U1.10 (B), U2.10 (B), U3.10 (B); also elsewhere on the board
C: U1.9 (C), U2.9 (C), U3.9 (C); also elsewhere on the board
GND: C54.2, C55.2, C56.2, C57.2, C58.2, C59.2, C60.2, C61.2, J3.3, J4.3, J5.3, J6.3, P3.3, P3.5, P3.6, P3.9, P3.11, P3.12, P3.15, P3.18, R32.2, U1.6 (Inh), U1.7 (VEE), U1.8 (VSS), U2.6 (Inh), U2.7 (VEE), U2.8 (VSS), U3.7 (VEE), U3.8 (VSS); also elsewhere on the board
I_ENABLE: R27.2; also elsewhere on the board
unnamed: R1.1, U4.1 (Set)
unnamed: R1.2, R3.1, U3.3 (X)
unnamed: R2.1, U4.4 (Out)
unnamed: R2.2, R3.2
PT100_Diff+: U1.3 (X); also elsewhere on the board
PT100_Diff-: U2.3 (X); also elsewhere on the board

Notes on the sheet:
Header de extensão 4 sensores
1mA

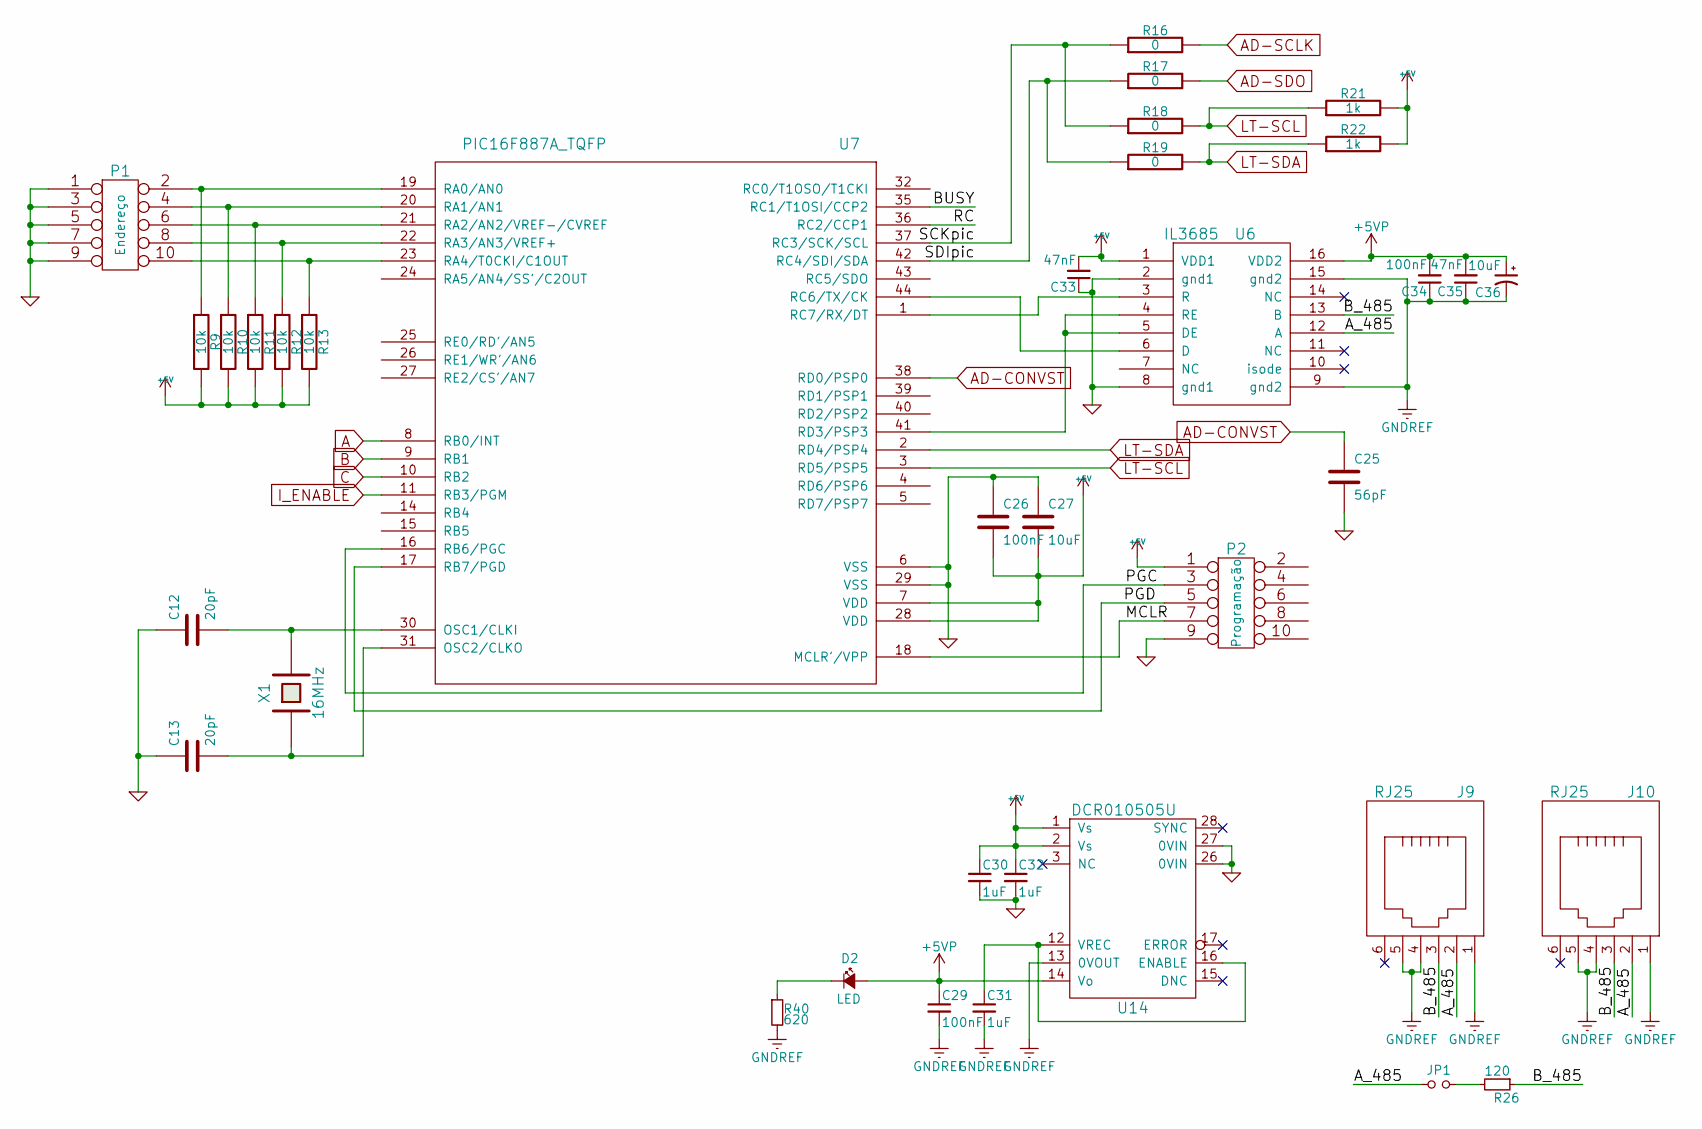
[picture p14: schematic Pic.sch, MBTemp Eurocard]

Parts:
C12, C13: 20pF
C25: 56pF
C26: 100nF
C27: 10uF
C29, C34: 100nF; C_0805
C30, C31, C32: 1uF; C_0805
C33, C35: 47nF; C_0805
C36: 10uF; TantalC_SizeR_EIA-2012
D2: LED; LED_para_painel_KINGBRIGHT
J9, J10: RJ25
JP1: Jumper_NO_Small; Pin_Header_Straight_1x02
P1: Endereço
P2: Programação
R9, R10, R11, R12, R13: 10k
R16, R17, R18, R19: 0
R21, R22: 1k
R26: 120; R_0805
R40: 620; R_0805
U6: IL3685
U7: PIC16F887A_TQFP
U14: DCR010505U; DCR01XXXXU
X1: 16MHz

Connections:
+5V: C26.2, C27.2, C30.1, C32.1, C33.2, P2.1, R9.2, R10.2, R11.2, R12.2, R13.2, R21.2, R22.2, U6.1 (VDD1), U7.7 (VDD), U7.28 (VDD), U14.1 (Vs), U14.2 (Vs); also elsewhere on the board
+5VP: C29.1, C34.2, C35.2, C36.1, D2.2 (A), U6.16 (VDD2), U14.14 (Vo)
/PIC/A_485: J9.2, J10.2, JP1.1, U6.12 (A)
/PIC/BUSY: U7.35 (RC1/T1OSI/CCP2)
/PIC/B_485: J9.3, J10.3, R26.1, U6.13 (B)
/PIC/RC: U7.36 (RC2/CCP1)
/PIC/SCKpic: R16.1, R18.1, U7.37 (RC3/SCK/SCL)
/PIC/SDIpic: R17.1, R19.1, U7.42 (RC4/SDI/SDA)
A: U7.8 (RB0/INT); also elsewhere on the board
AD-CONVST: C25.1, U7.38 (RD0/PSP0); also elsewhere on the board
AD-SCLK: R16.2; also elsewhere on the board
AD-SDO: R17.2; also elsewhere on the board
B: U7.9 (RB1); also elsewhere on the board
C: U7.10 (RB2); also elsewhere on the board
GND: C12.1, C13.1, C25.2, C26.1, C27.1, C30.2, C32.2, C33.1, J9.0, J10.0, P1.1, P1.3, P1.5, P1.7, P1.9, P2.9, U6.2 (gnd1), U6.8 (gnd1), U7.6 (VSS), U7.29 (VSS), U14.26 (0VIN), U14.27 (0VIN); also elsewhere on the board
GNDREF: C29.2, C31.2, C34.1, C35.1, C36.2, J9.1, J9.4, J9.5, J10.1, J10.4, J10.5, R40.2, U6.9 (gnd2), U6.15 (gnd2), U14.13 (0VOUT)
I_ENABLE: U7.11 (RB3/PGM); also elsewhere on the board
LT-SCL: R18.2, R21.1, U7.3 (RD5/PSP5); also elsewhere on the board
LT-SDA: R19.2, R22.1, U7.2 (RD4/PSP4); also elsewhere on the board
unnamed: C12.2, U7.30 (OSC1/CLKI), X1.2
unnamed: C13.2, U7.31 (OSC2/CLKO), X1.1
unnamed: C31.1, U14.12 (VREC), U14.16 (ENABLE)
unnamed: D2.1 (K), R40.1
unnamed: JP1.2, R26.2
unnamed: P1.2, R9.1, U7.19 (RA0/AN0)
unnamed: P1.4, R10.1, U7.20 (RA1/AN1)
unnamed: P1.6, R11.1, U7.21 (RA2/AN2/VREF-/CVREF)
unnamed: P1.8, R12.1, U7.22 (RA3/AN3/VREF+)
unnamed: P1.10, R13.1, U7.23 (RA4/T0CKI/C1OUT)
unnamed: P2.3, U7.16 (RB6/PGC)
unnamed: P2.5, U7.17 (RB7/PGD)
unnamed: P2.7, U7.18 (MCLR'/VPP)
unnamed: U6.3 (R), U7.1 (RC7/RX/DT)
unnamed: U6.4 (RE), U6.5 (DE), U7.41 (RD3/PSP3)
unnamed: U6.6 (D), U7.44 (RC6/TX/CK)

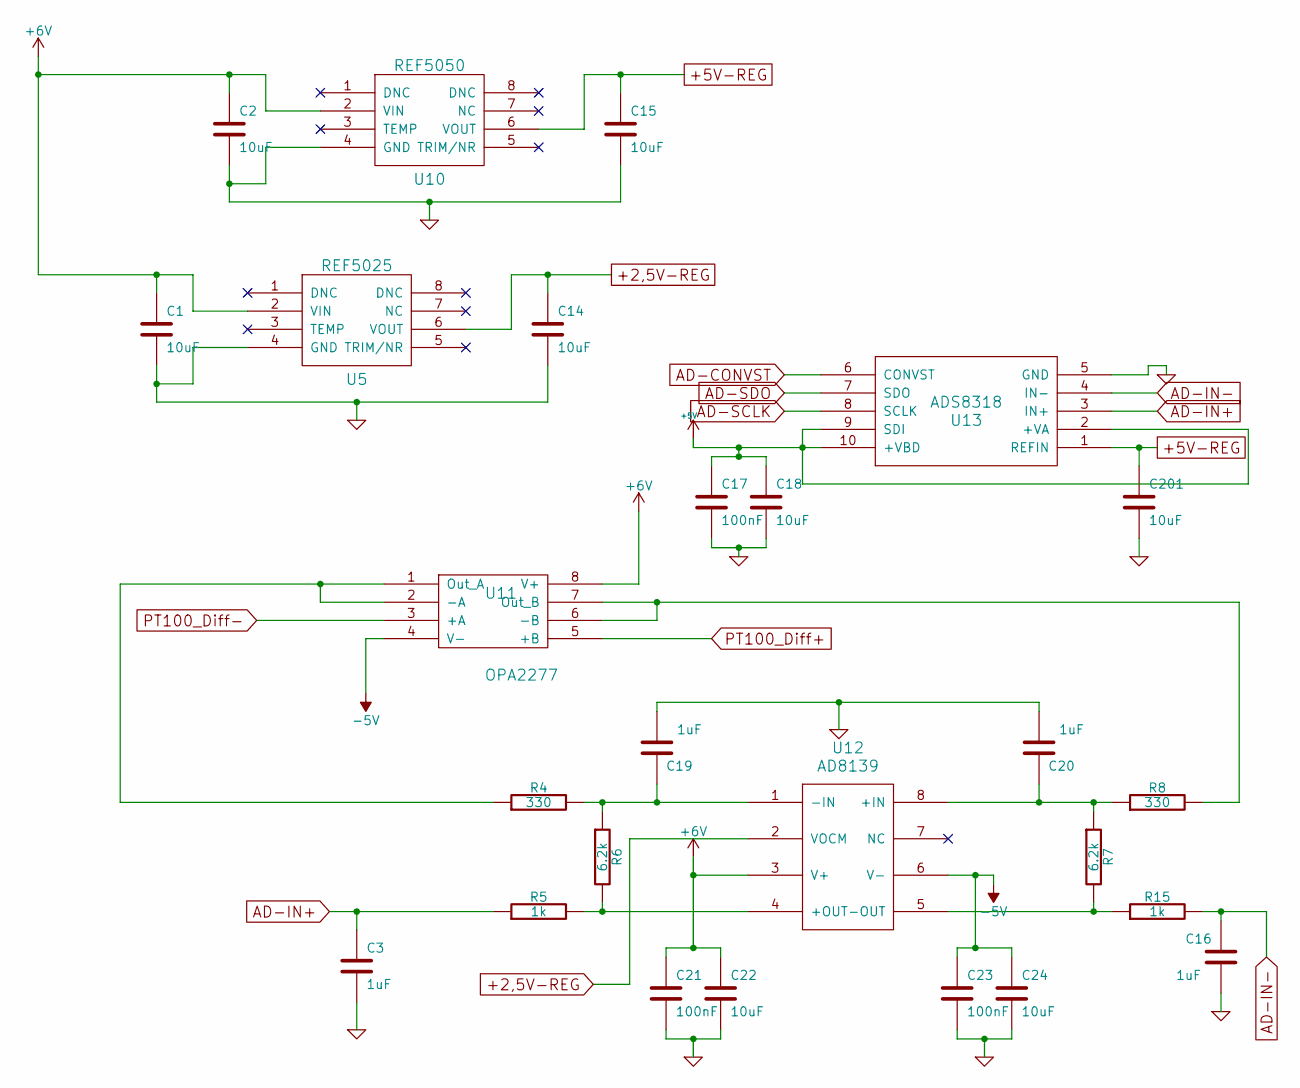
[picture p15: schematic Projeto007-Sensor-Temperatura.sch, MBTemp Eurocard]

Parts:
C1, C2, C14, C15, C18, C22, C24, C201: 10uF
C3, C16, C19, C20: 1uF
C17, C21, C23: 100nF
R4, R8: 330
R5, R15: 1k
R6, R7: 6.2k
U5: REF5025
U10: REF5050
U11: OPA2277
U12: AD8139
U13: ADS8318

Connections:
+2,5V-REG: C14.1, U5.6 (VOUT), U12.2 (VOCM)
+5V: C17.1, C18.1, U13.2 (+VA), U13.9 (SDI), U13.10 (+VBD); also elsewhere on the board
+5V-REG: C15.1, C201.1, U10.6 (VOUT), U13.1 (REFIN)
+6V: C1.1, C2.1, C21.1, C22.1, U5.2 (VIN), U10.2 (VIN), U11.8 (V+), U12.3 (V+); also elsewhere on the board
-5V: C23.1, C24.1, U11.4 (V-), U12.6 (V-); also elsewhere on the board
AD-CONVST: U13.6 (CONVST); also elsewhere on the board
AD-IN+: C3.1, R5.1, U13.3 (IN+)
AD-IN-: C16.1, R15.2, U13.4 (IN-)
AD-SCLK: U13.8 (SCLK); also elsewhere on the board
AD-SDO: U13.7 (SDO); also elsewhere on the board
GND: C1.2, C2.2, C3.2, C14.2, C15.2, C16.2, C17.2, C18.2, C19.2, C20.2, C21.2, C22.2, C23.2, C24.2, C201.2, U5.4 (GND), U10.4 (GND), U12.9, U13.5 (GND); also elsewhere on the board
unnamed: C19.1, R4.2, R6.1, U12.1 (-IN)
unnamed: C20.1, R7.1, R8.1, U12.8 (+IN)
unnamed: R4.1, U11.1 (Out_A), U11.2 (-A)
unnamed: R5.2, R6.2, U12.4 (+OUT)
unnamed: R8.2, U11.6 (-B), U11.7 (Out_B)
unnamed: R7.2, R15.1, U12.5 (-OUT)
PT100_Diff+: U11.5 (+B); also elsewhere on the board
PT100_Diff-: U11.3 (+A); also elsewhere on the board

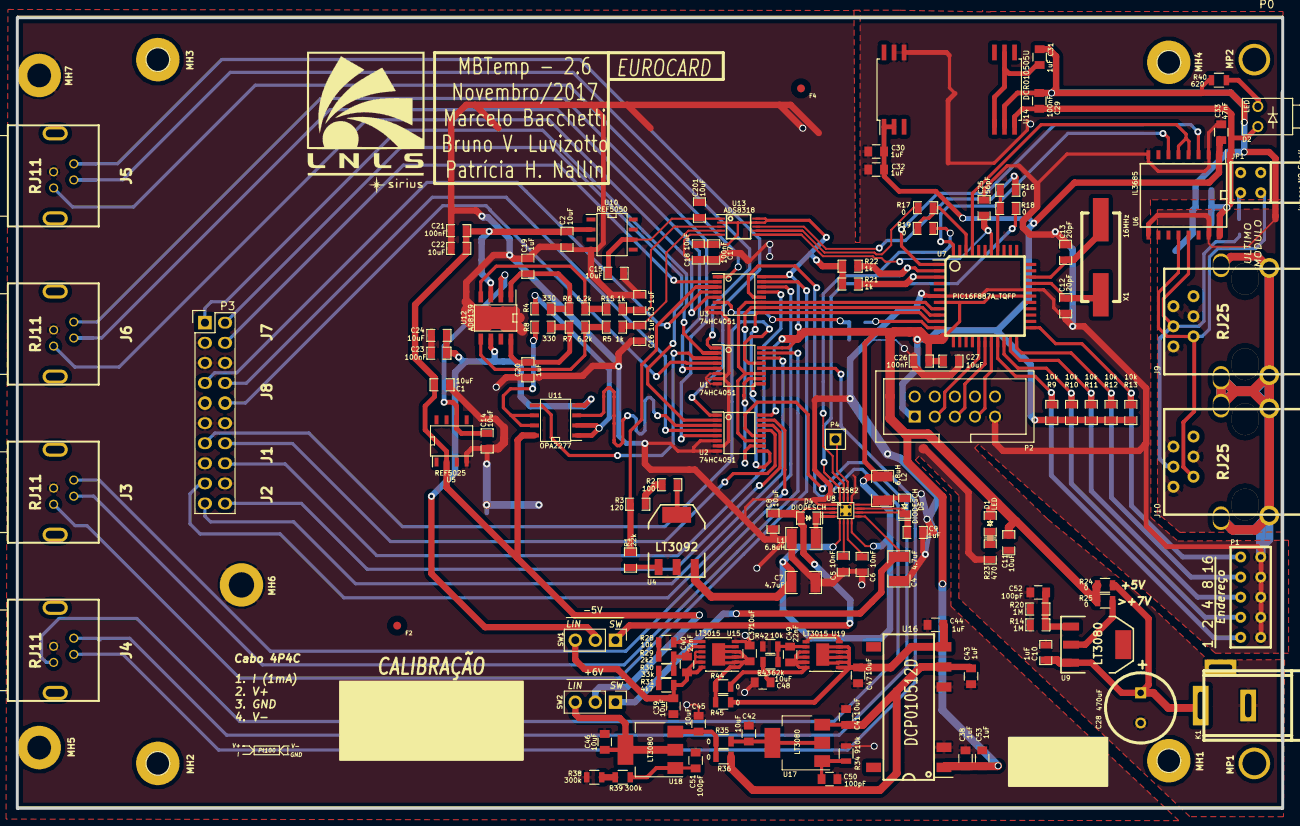
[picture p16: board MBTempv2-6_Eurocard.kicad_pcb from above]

Board: 2 copper layers, 160.0 x 100.0 mm, 149 parts (0 on the bottom side), 103 nets.

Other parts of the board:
F1, F2, F3, F4: Fiducial; Fiducial_1mm_Dia_2.54mm_Outer_CopperBottom
P0: C64AC; Eurocard_template

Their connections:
GND: P0.2; also elsewhere on the board
